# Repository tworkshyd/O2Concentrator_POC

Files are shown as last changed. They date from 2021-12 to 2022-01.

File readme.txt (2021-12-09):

#### Log of Firmware development ################

 5th May 2021 
	# development started

17th May 2021 
	# 1st test build released
         - O2 generation logic as per oxikit implemented

22th May 2021
	# 2nd test build released 
	 - ON/OFF switch incorporated

08 Sep 2021
	# 3rd test build working on first hand prototyped hardware
		with 3_2_valve_versions_900gms_08092021

13 Sep 2021
	# Board bringup for Rev 1.0 h/w started

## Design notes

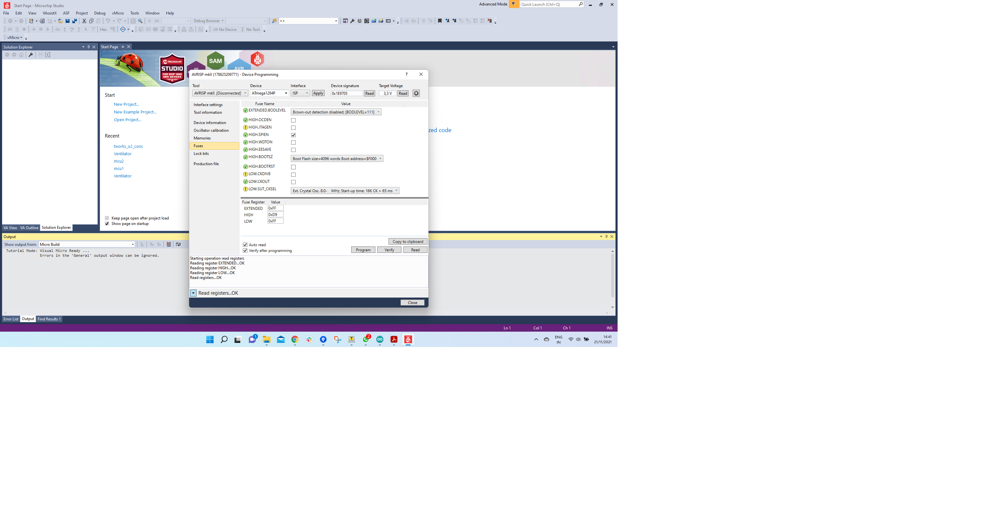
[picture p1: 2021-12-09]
tworks_o2_cons_docs/Fuse-bits-to-program.png

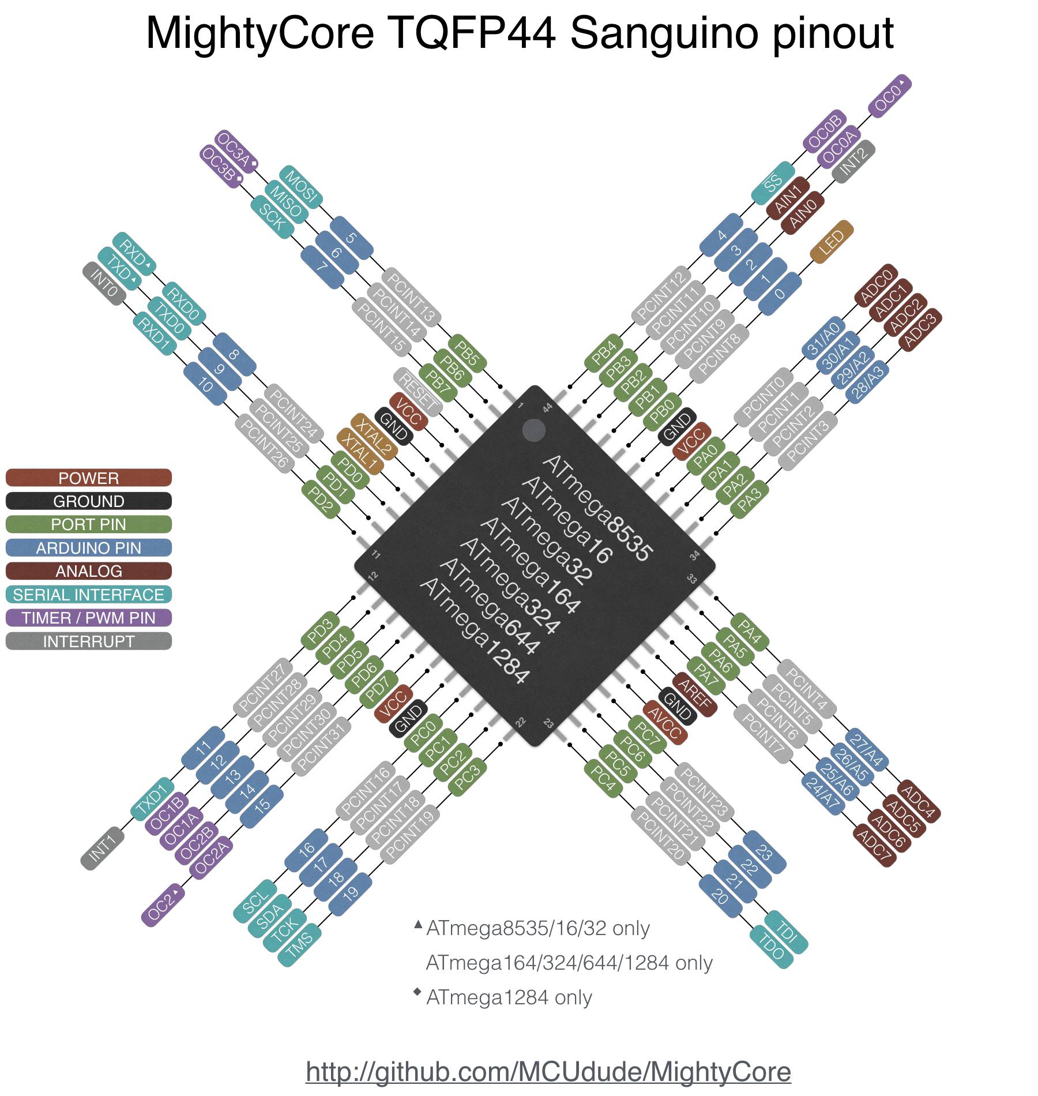
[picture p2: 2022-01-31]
tworks_o2_cons_docs/Atmega-1284p-pin-out.jpg

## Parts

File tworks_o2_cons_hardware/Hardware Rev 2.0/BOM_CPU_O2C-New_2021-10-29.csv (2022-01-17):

ID | Name | Designator | Footprint | Quantity | Manufacturer Part | Manufacturer | Supplier | Supplier Part | Price
1 | Battery Holder CR2032 | B1 | BATTERY_CR2032 | 1
2 | 22pF | C1,C2 | C1206 | 2
3 | 100nF | C3,C6,C7,C8,C9,C10,C11,C12,C13,C15,C17,C18,C19,DCU3,DCU4,DCU5,DCU8 | C1206 | 17
4 | 10u | C4,C5 | EIA3216 | 2 | ?
5 | 0.33uF | C14 | C1206 | 1
6 | 1uF | C16 | C1206 | 1
7 | 47uF-100V-SMD | C20 | CAPAE1300X1400N | 1
8 | 1nF-2KV-1206-AVX | C21,C22 | CAPC3317X180N | 2
9 | 10uF-50V-1206 | C23,C24 | CAPC3216X190N | 2
10 | 330uF-50V-SMD | C25,C26 | CAPAE1300X1400N | 2
11 | 0.47mfd | C27 | 1206 | 1 | ?
12 | 33mfd | C28 | CAP-D5.0XF2.0 | 1 | ?
13 | M7_C84184 | D1,D2,D3 | SMA_L4.3-W2.6-LS5.2-RD | 3 | M7 | DYELEC | LCSC | C84184 | 0.011
14 | SM712 | D4 | SOT-23_L2.9-W1.3-P1.90-LS2.4-BR | 1 | SM712 | Yenji | LCSC | C127543
15 | TFZVTR9.1B | D5 | SOD-323HE_L2.0-W1.4-LS2.5-RD | 1 | TFZVTR9.1B | ROHM Semicon | LCSC | C117743 | 0.162
16 | FL2D-13-471R3 | FL1 | FL2D13471R3 | 1
17 | BOXHDR 2.54_2x10 | J1 | HDR-M-2.54_2X10 | 1 |  |  | LCSC | C124359 | 0.136
18 | HDR-F-2.54_2x3 | J2 | HDR-F-2.54_2X3 | 1 |  |  | LCSC | C65114 | 0.025
19 | BOXHDR 2.54_2x6 | J3 | HDR-M-2.54_2X6 | 1 |  |  | LCSC | C124388 | 0.071
20 | Berg 2 Pin | JMP1,JMP2,JMP3 | HDR-F-2.54_1X2 | 3 |  |  | LCSC | C49661 | 0.03
21 | Berg 3 Pin | JMP4 | HDR-F-2.54_1X3 | 1 |  |  | LCSC | C146690 | 0.068
22 | Berg 2 Pin | JMP5,JP4 | HDR-M-2.54_1X2 | 2 |  |  | LCSC | C124375 | 0.017
23 | Relimate 3 Pin | JP1,JP2 | HDR-M-2.54_1X3 | 2 |  |  | LCSC | C180248 | 0.236
24 | Relimate 3 Pin | JP3 | HDR-F-2.54_1X3 | 1 |  |  | LCSC | C146690 | 0.068
25 | 10uH | L1 | L_AXIAL-0.4 | 1
26 | LED 1206 Yellow | LED1,LED2 | LED 1206 RED | 2
27 | LED 1206 White | LED3 | LED 1206 RED | 1
28 | LED 1206 RED | LED4,LED5,LED6,LED7,LED8,LED9,LED10 | LED 1206 RED | 7
29 | CONN-TH_2P-P5.00 | P1,P2,P3,P4,P6 | CONN-TH_2P-P5.00 | 5 |  |  | LCSC
30 | 2N7002LT1H | Q1,Q2,Q3,Q5 | SOT23-3 | 4
31 | FQB22P10TM | Q4 | TO-263-3_L10.2-W10.7-P5.08-LS16.2-BR | 1 | FQB22P10TM | ON Semicon | LCSC | C108357 | 2.4
32 | BC847A | Q5~ | SOT-23-3_L2.9-W1.3-P1.90-LS2.4-BR | 1 | BC847A | Shenzhen Jinyu Semicon | LCSC | C259985 | 0.009
33 | 100R | R1,R2,R5 | R1206 | 3
34 | 99.9R | R3,R4 | AXIAL-0.4 | 2 | ?
35 | 120R | R6 | R1206 | 1
36 | 180R | R7,R8 | AXIAL-0.4 | 2 | ?
37 | 301R | R9,R10 | AXIAL-0.4 | 2 | ?
38 | 330R | R11,R12,R13,R14,R15,R15~ | R1206 | 6
39 | 500R | R16,R17 | AXIAL-0.4 | 2 | ?
40 | 510R | R18,R19,R20,R21 | R1206 | 4
41 | 680R | R22,R23 | R1206 | 2
42 | 750R | R24 | R1206 | 1
43 | 1k | R25,R26 | AXIAL-0.4 | 2 | ?
44 | 1.2K | R27,R28,R29,R30 | R1206 | 4
45 | 3.3K | R31,R32,R33,R34,R35 | R1206 | 5
46 | 3.32K | R36 | R1206 | 1
47 | 4.7K | R37,R38 | R1206 | 2
48 | 4.99k | R39,R40,R41,R42 | AXIAL-0.4 | 4 | ?
49 | 5.1K | R43,R44 | R1206 | 2
50 | 10K | R45,R46,R48,R49,R50,R51,R52 | R1206 | 7
51 | 10k | R47 | R1206 | 1
52 | 100k | R53 | R1206 | 1
53 | 105K | R54,R55 | AXIAL-0.4 | 2 | ?
54 | 0R | R56 | R1206 | 1
55 | SRD-05VDC-SL-C | RLY1,RLY2,RLY3 | RELAY-TH_SRD-XXVDC-XL-C | 3 | SRD-05VDC-SL-C | SONGLE | LCSC | C35449 | 0.418
56 | BUZZERPTH | SG1 | BUZZER-12MM | 1
57 | TestPin | TP1,TP2,TP3,TP4,TP5 | TESTPIN | 5
58 | ATMEGA164PA-AU | U1 | TQFP-44_L10.0-W10.0-P0.80-LS12.0-BL | 1 | ATMEGA164PA-AU | Microchip Tech | LCSC | C220668 | 2.902
59 | MAX485ECSA+ | U2 | SOIC-8 | 1
60 | AT24C64D-SSHM-B | U3 | SOIC-8_L4.9-W3.9-P1.27-LS6.0-BL | 1 | AT24C64D-SSHM-B | MICROCHIP | LCSC | C116707 | 1.777
61 | DS1307ZN+ | U4 | SOP-8_L4.9-W3.9-P1.27-LS6.0-BL | 1 | DS1307ZN+ | MAXIM | LCSC | C26858 | 1.587
62 | NUF8402MNT4G | U5,U6,U7 | DFN-16_L4.0-W1.6-P0.50-BL-EP | 3 | NUF8402MNT4G | ON Semicon | LCSC | C233420 | 0.416
63 | ULN2803ADWR | U8 | SOIC-18_L11.6-W7.5-P1.27-LS10.3-BL | 1 | ULN2803ADWR | TI | LCSC | C9683 | 2.443
64 | MPX5100AP | U9 | MPX5100AP | 1 | MPX5100AP | NXP Semiconductors | Mouser | 841-MPX5100AP
65 | MPXV5100GP | U10 | MPXV5100GP | 1
66 | INA826AIDR | U11,U12 | SOIC-8_150MIL | 2 | INA826AIDR | TI | LCSC | C38433 | 3.949
67 | MCP6002-ESN | U13 | SOIC-8 | 1
68 | ADS1115QDGSRQ1 | U14 | MSOP10 | 1
69 | ICL7660AIBAZA-T | U15 | SOIC-8_150MIL | 1 | ICL7660AIBAZA-T | Intersil | LCSC | C7881 | 0.985
70 | URB2405S-10WR3 | U16 | PWRM-TH_URBXXXXS-6WR3 | 1 | URB2405S-10WR3 | MORNSUN Guangzhou S& T | LCSC | C970774 | 13.739
71 | LM3940IMP-3.3NOPB | U17 | SOT-223 | 1
72 | 16MHz | X1 | HC-49S_L11.0-W4.4-P4.88 | 1 | 49S DIP Crystal insulation film | YXC | LCSC | C35018 | 0.007
73 | 32.768KHz | X2 | 32K_CRYSTAL_BODYGND_FPRNT_MBR_2 | 1 | TDXLF-308 32.768KHZ 12.5PF 20PPM | TAE | LCSC | C145164 | 0.067
74 | XBEE-1B1 | XB1 | XBEE-1 | 1

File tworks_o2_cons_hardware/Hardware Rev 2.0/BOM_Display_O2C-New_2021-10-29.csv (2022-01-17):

ID | Name | Designator | Footprint | Quantity | Manufacturer Part | Manufacturer | Supplier | Supplier Part | Price
1 | 100nF | C1,C2,C3,DCNP1,DCNP2,DCNP3,DCNP4,DCU1,DCU2,DCU2-1,DCU2-2,DCU2-3 | C1206 | 12
2 | SUPERCAP 1F | C9 | SUPERCAPACITOR 1F | 1
3 | 1N4007R | D1 | DO-41_BD2.4-L4.7-P8.70-D0.9-RD | 1 | 1N4007R | Chongqing Pingwei Tech | LCSC | C432606 | 0.016
4 | 0.56" 7 segment display common cathode | DISP1,DISP2,DISP3,DISP4,DISP5 | LEDSEG_1_0.56_CATHODE | 5 | SC56-11SYKWA | Kingbright | RS-Online | 877-1555
5 | HDR-M-2.54_1x3 | J1,J2 | HDR-M-2.54_1X3 | 2 |  |  | LCSC | C180248 | 0.236
6 | HDR-M-2.54_2x10 | J3 | HDR-M-2.54_2X10 | 1 |  |  | LCSC | C124359 | 0.136
7 | HDR-M-2.54_1x4 | J4,J5 | HDR-M-2.54_1X4 | 2 |  |  | LCSC | C124378 | 0.028
8 | HDR-M-2.54_2x3 | JTAG1 | HDR-M-2.54_2X3 | 1 |  |  | LCSC | C65114 | 0.025
9 | 5050 SMD LED | LED1 | LED SMD 5050 | 1 | LEDSMD5050
10 | WS2812B-5050RGB | NPLED1,NPLED2,NPLED3,NPLED4 | LED-SMD_4P-L5.0-W5.0-BR_WS2812B-5050RGB | 4 | WS2812B-5050RGB | null | LCSC | C2838584
11 | BC558B | Q1 | TO-92-3_L4.9-W3.7-P1.27-L | 1 | BC558B | LGE | LCSC | C713619 | 0.019
12 | 330R | R1 | R1206 | 1
13 | 470R | R2,R3 | R1206 | 2
14 | 9.53K | R4 | R1206 | 1
15 | 10K | R5,R6,R7,R8,R9,R10,R11 | R1206 | 7
16 | 10k | R12,R13 | R1206 | 2
17 | BUZZERPTH | SG1 | BUZZER-12MM | 1
18 | MAX7219CWG+T | U1 | SOIC-24 | 1
19 | ATTINY85-20SU | U2 | SOIC-8_L5.3-W5.3-P1.27-LS8.0-BL | 1 | ATTINY85-20SU | MICROCHIP | LCSC | C89852 | 6.043
20 | XL74LS20 | U3 | SOP-14_L8.6-W3.9-P1.27-LS6.0-BL | 1 | XL74LS20 | XINLUDA | LCSC | C556253 | 0.151
21 | 100K | VR1 | RES-ADJ-TH_3296W | 1 | Pot-100R | ReliaPro | LCSC | C13649

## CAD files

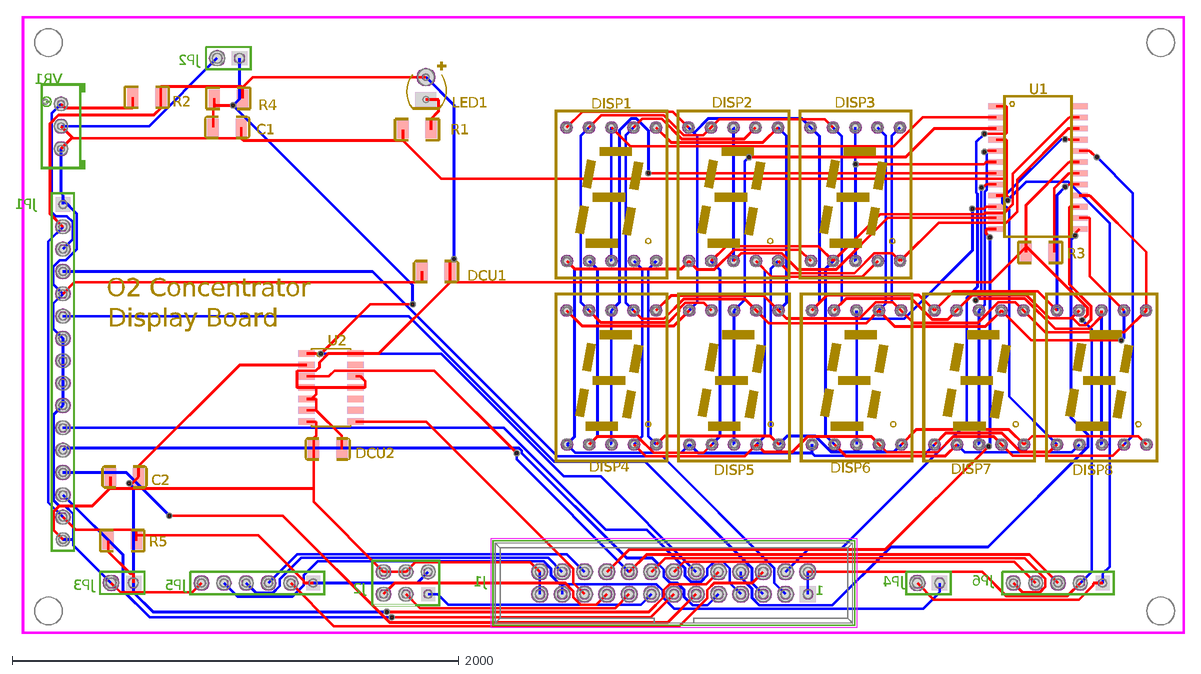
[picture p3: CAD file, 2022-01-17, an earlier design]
tworks_o2_cons_hardware/Hardware Rev 1.0/PCB_O2Conc-Display_2_2021-08-23.dxf
Display Board
O2 Concentrator
JP5
VR1
J1
1
JP6
JP1
J2
JP2
JP3
JP4
U1
LED1
DCU1
DCU2
DISP3
DISP2
DISP1
DISP5
DISP6
DISP8
DISP7
DISP4
R3
R2
R1
U2
C1
C2
R4
R5

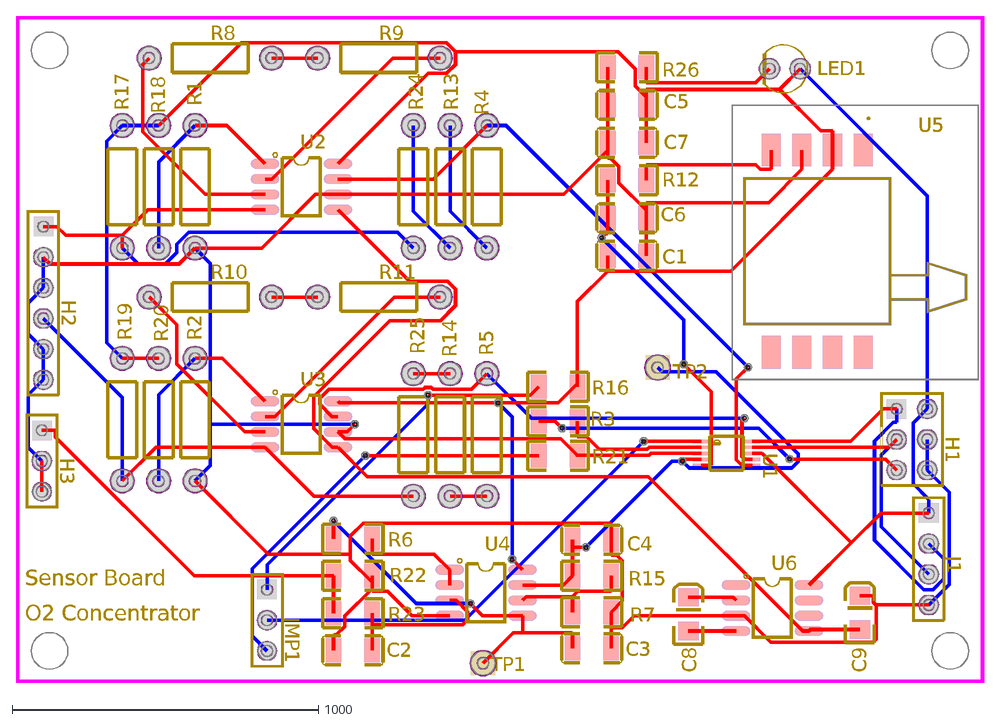
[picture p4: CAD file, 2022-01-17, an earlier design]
tworks_o2_cons_hardware/Hardware Rev 1.0/PCB_O2Conc_Sensorbrd_2021-08-23.dxf
O2 Concentrator
Sensor Board
J1
H2
R19
R20
R11
R5
R14
R25
R10
R2
R13
R9
R17
R18
R1
R8
R24
R4
U1
TP2
TP1
C3
C5
C6
C4
C2
C1
C7
JMP1
H3
U6
U5
U2
U3
C8
C9
H1
R23
R22
R12
R21
R16
R7
R15
R3
R6
U4
LED1
R26

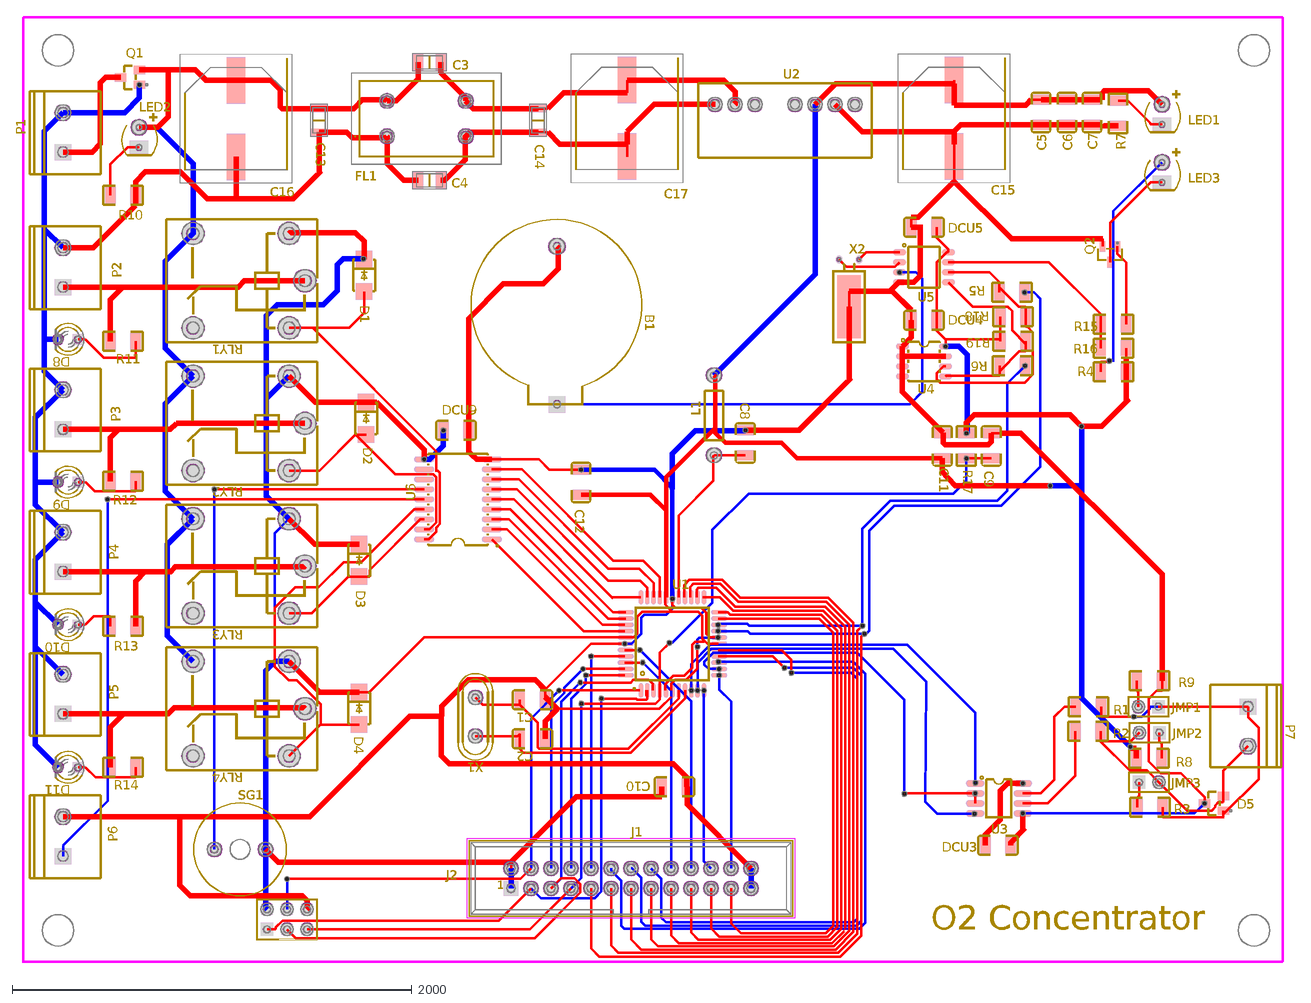
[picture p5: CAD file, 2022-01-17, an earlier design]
tworks_o2_cons_hardware/Hardware Rev 1.0/PCB_O2Concentrator_2021-08-23.dxf
O2 Concentrator
U6
D5
Q1
Q2
FL1
RLY2
RLY1
RLY3
RLY4
X2
B1
JMP3
JMP2
JMP1
D1
D3
D4
D2
P6
P5
P2
P3
P4
C17
C16
C15
U2
C4
C3
X1
LED3
LED2
LED1
J1
1
L1
C13
C14
D8
D9
D10
D11
C2
C1
DCU9
DCU3
C7
C12
C11
C10
C5
C9
C6
C8
U5
U3
J2
U4
R10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

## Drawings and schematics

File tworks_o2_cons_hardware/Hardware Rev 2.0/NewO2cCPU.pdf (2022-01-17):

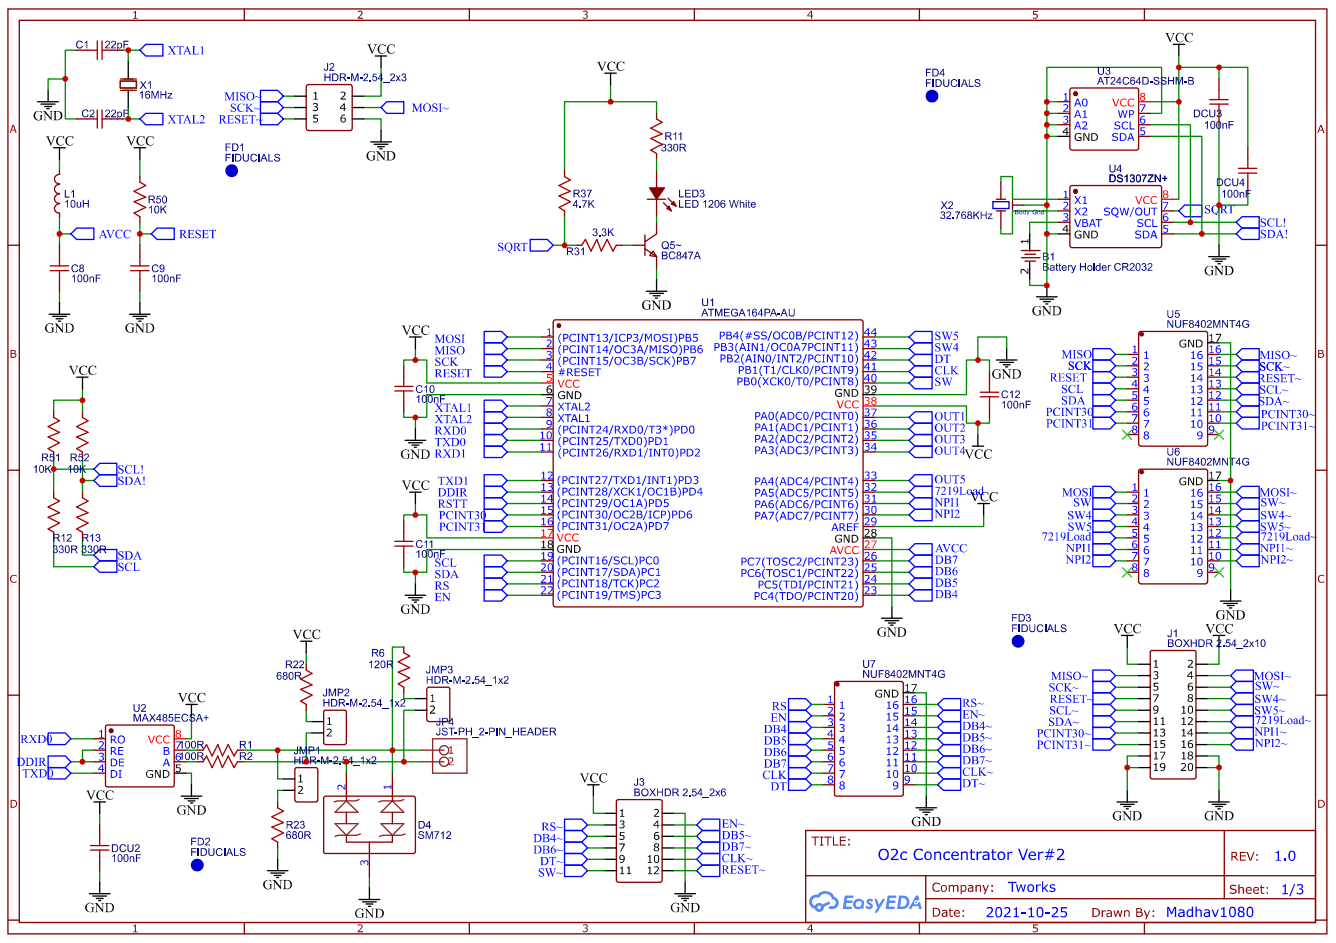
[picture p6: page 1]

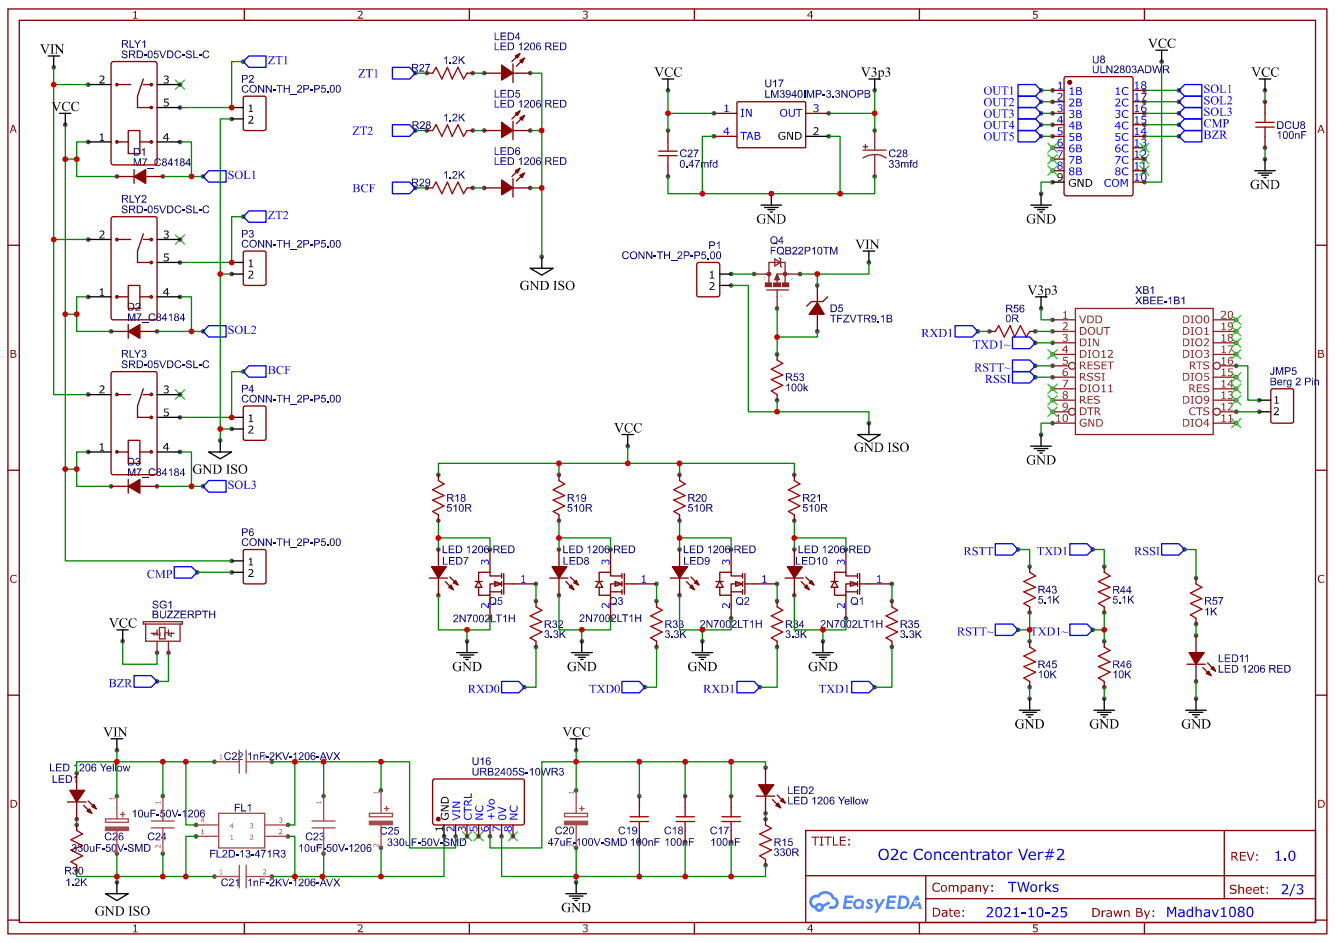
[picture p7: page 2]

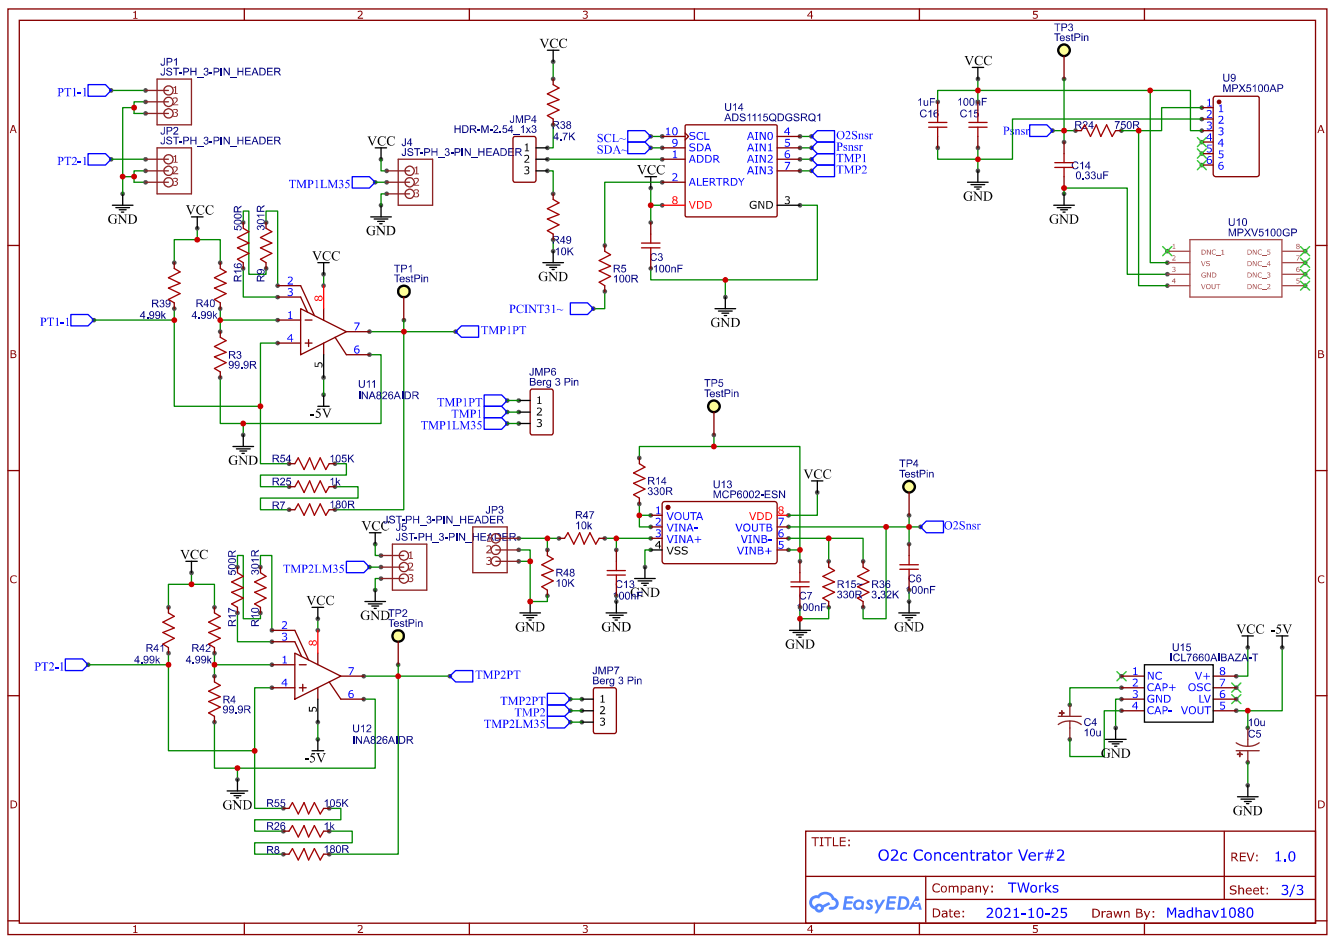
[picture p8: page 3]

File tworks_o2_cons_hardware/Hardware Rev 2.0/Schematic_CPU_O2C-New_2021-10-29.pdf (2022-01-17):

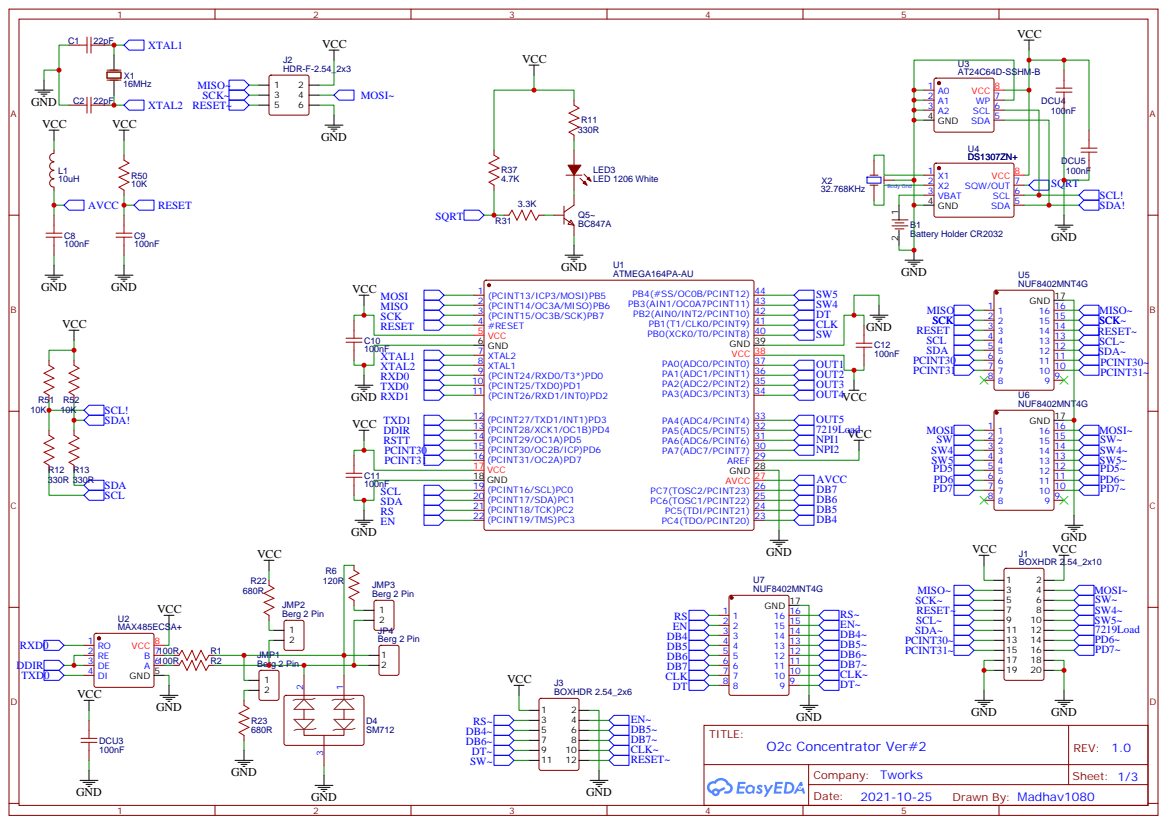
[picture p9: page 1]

# COM 10 8C 11 7C 12 6C 13 5C 14 4C 15 3C 16 2C 17 1C 18

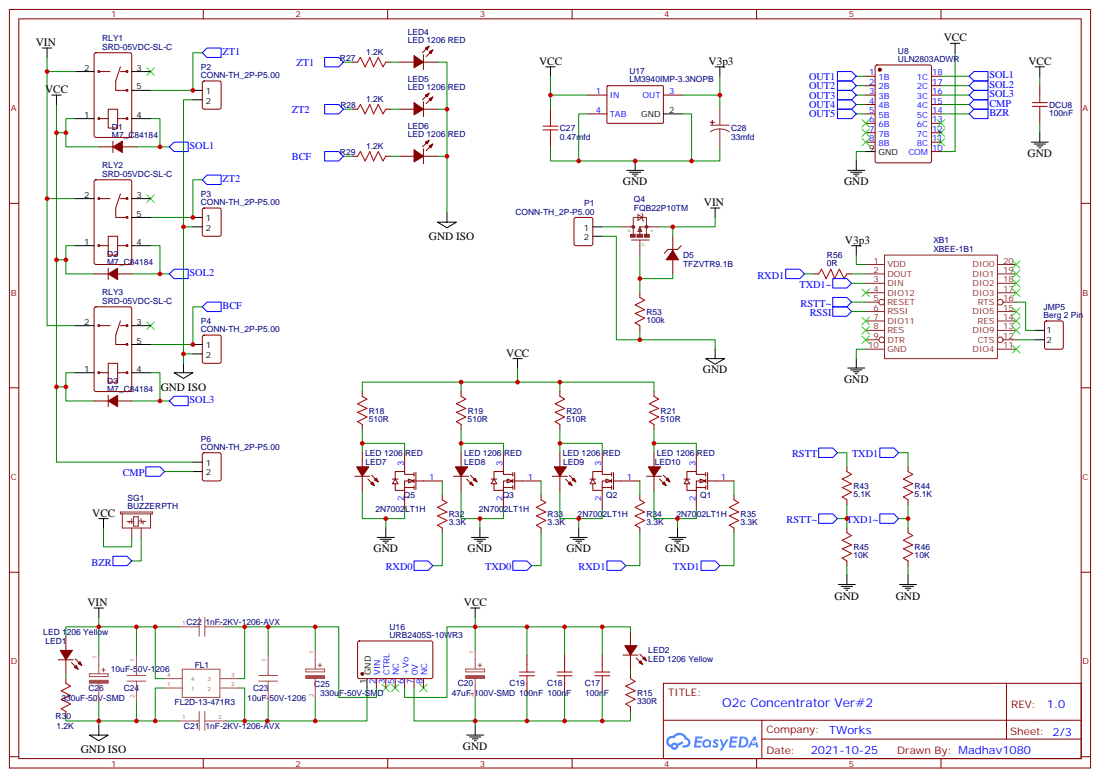
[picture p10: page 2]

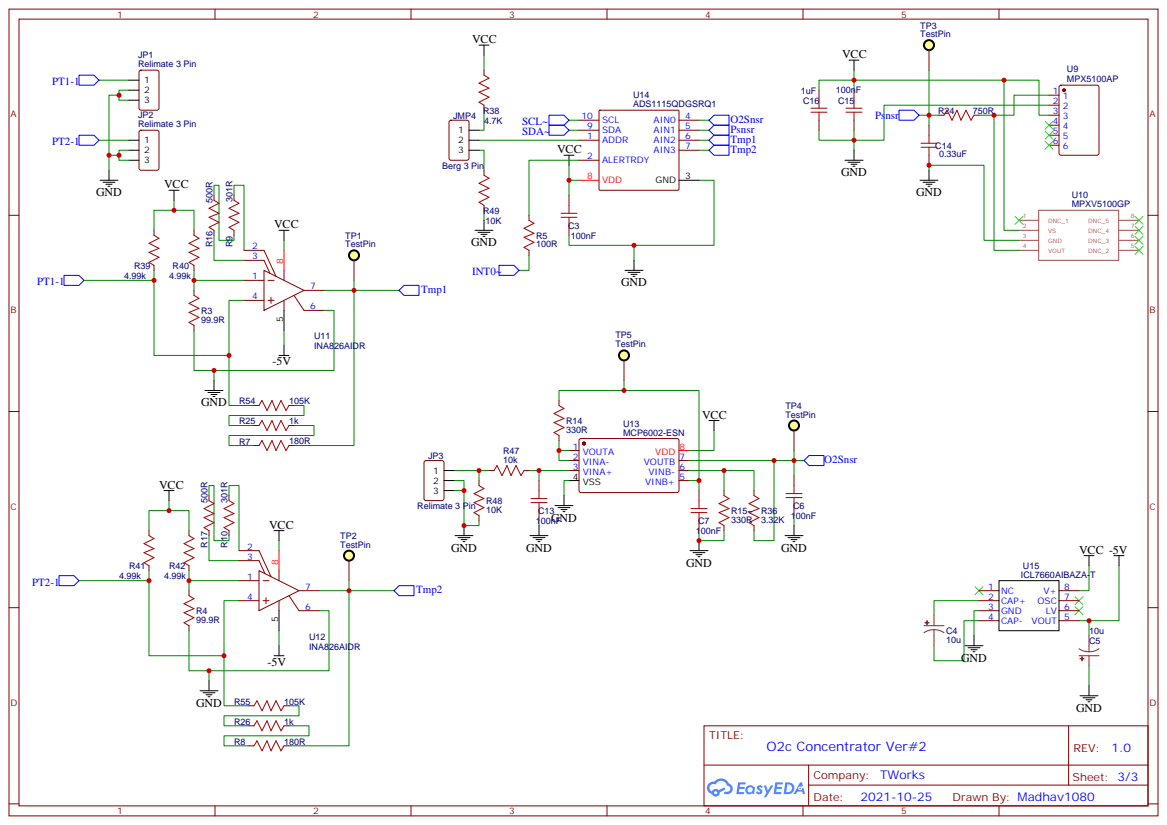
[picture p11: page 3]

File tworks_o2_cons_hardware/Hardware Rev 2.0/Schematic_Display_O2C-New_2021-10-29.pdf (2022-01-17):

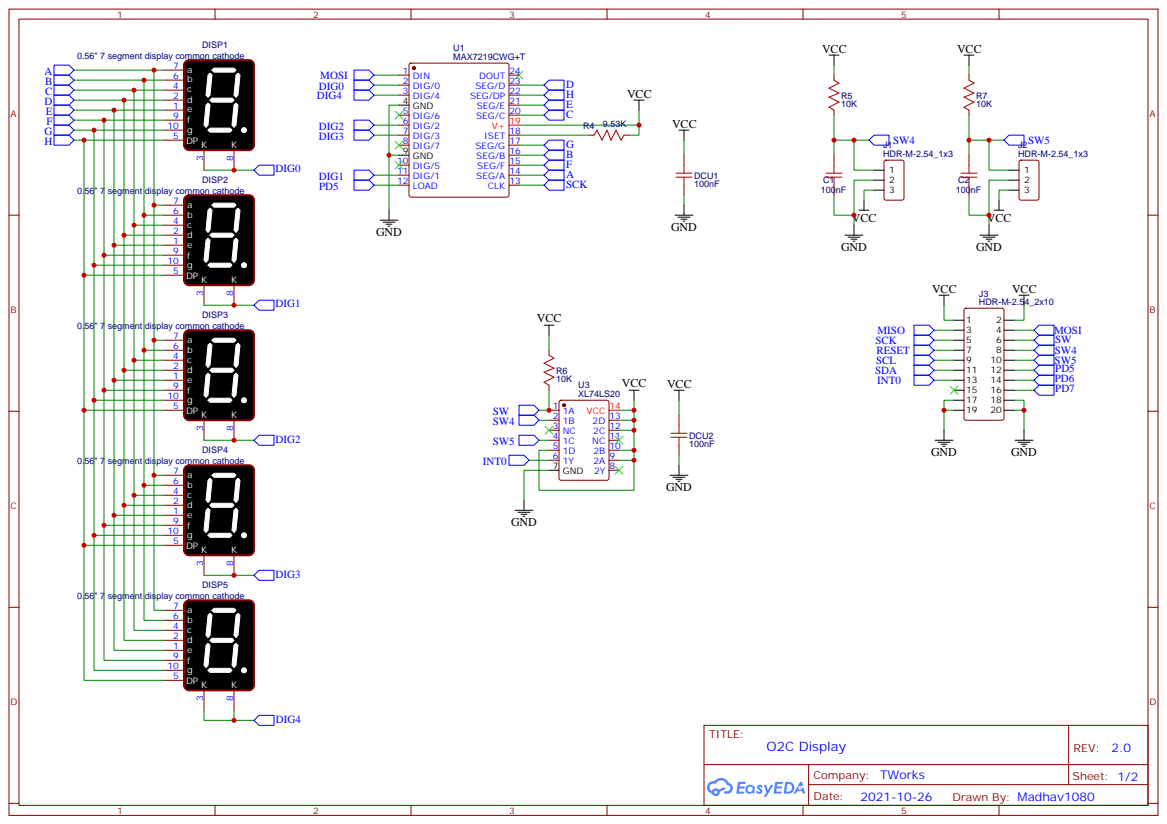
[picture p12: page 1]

0.56" 7 segment display common cathode

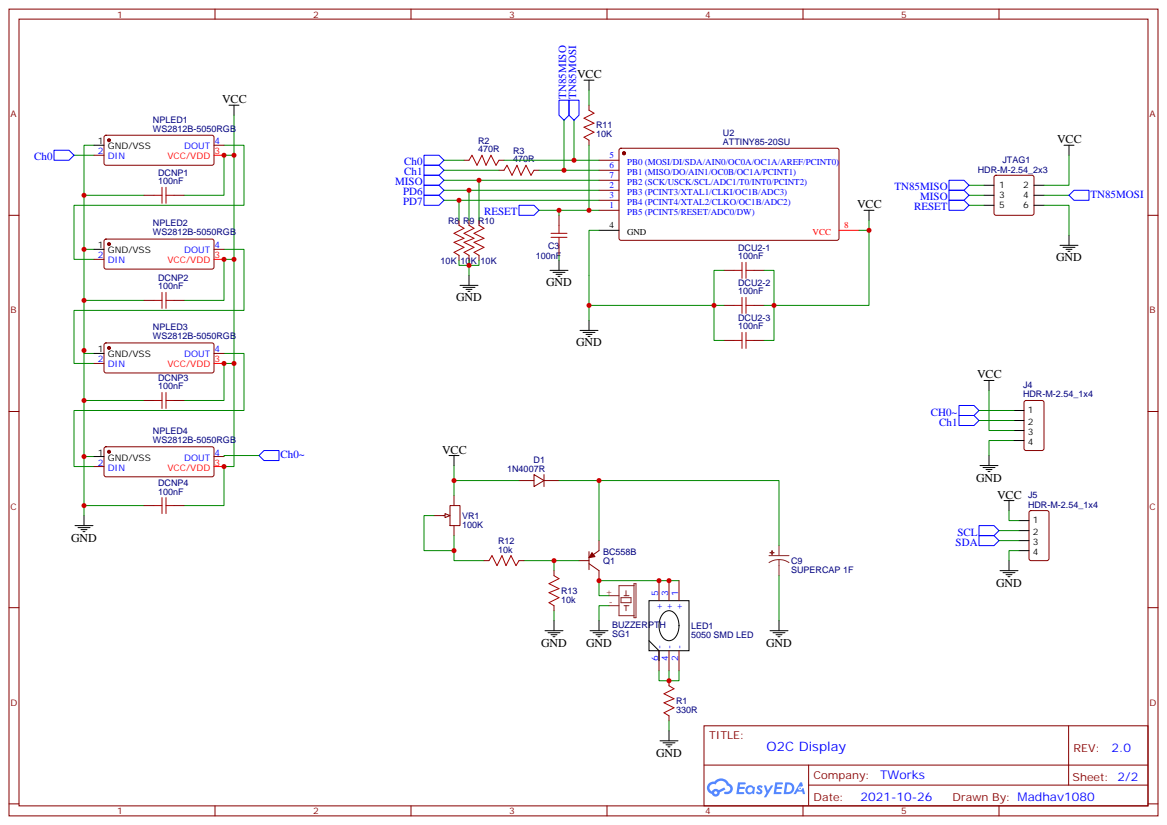
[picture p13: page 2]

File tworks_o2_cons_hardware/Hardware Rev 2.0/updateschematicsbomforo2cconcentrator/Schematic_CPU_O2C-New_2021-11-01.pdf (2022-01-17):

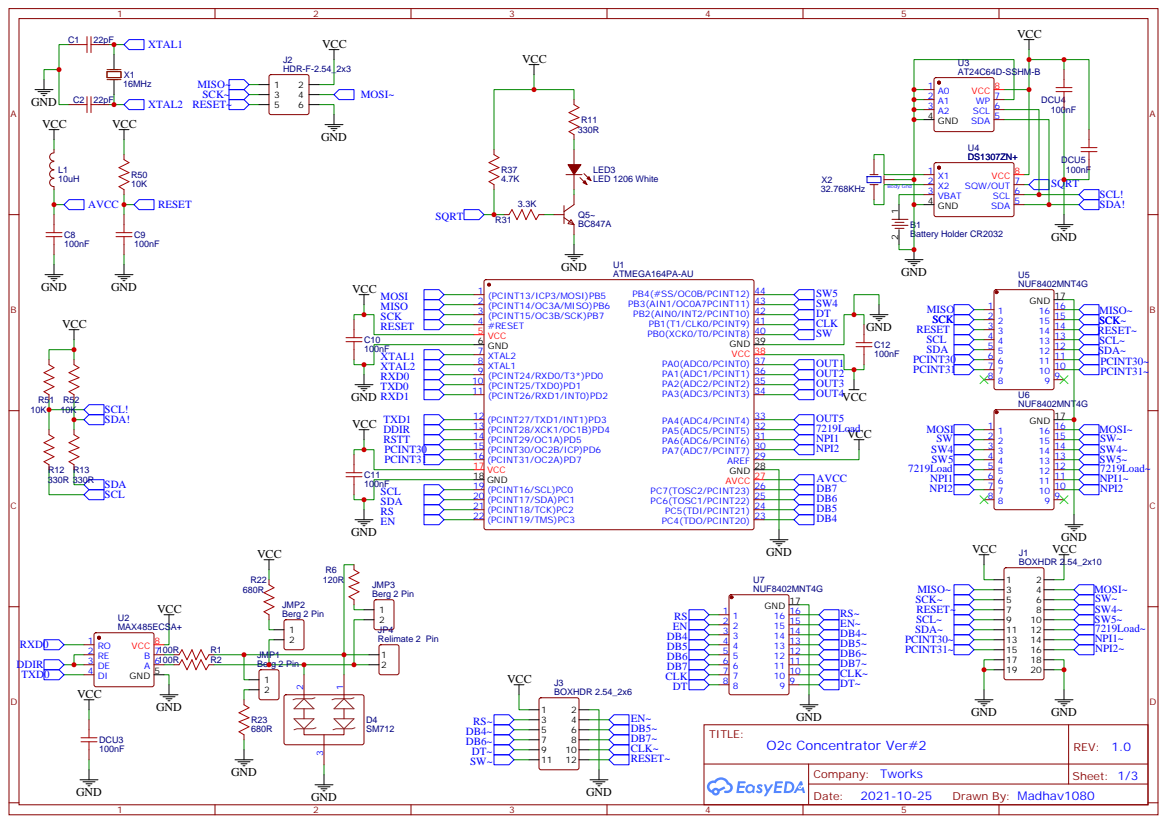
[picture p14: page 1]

# COM 10 8C 11 7C 12 6C 13 5C 14 4C 15 3C 16 2C 17 1C 18

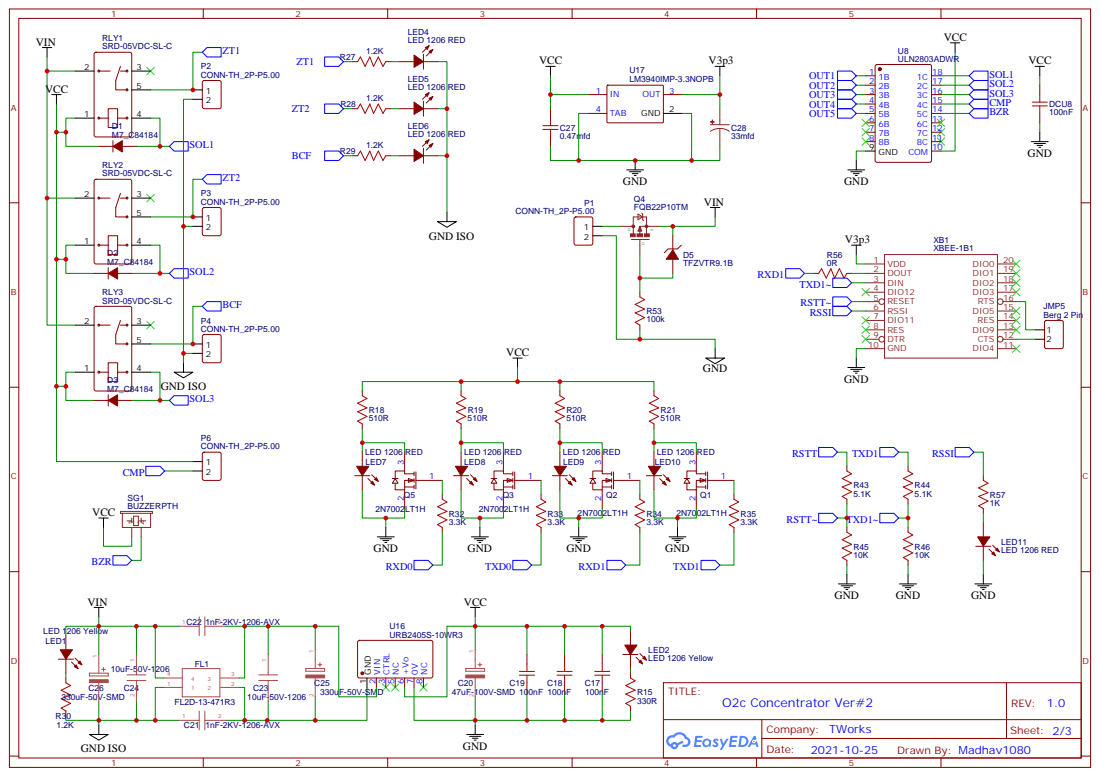
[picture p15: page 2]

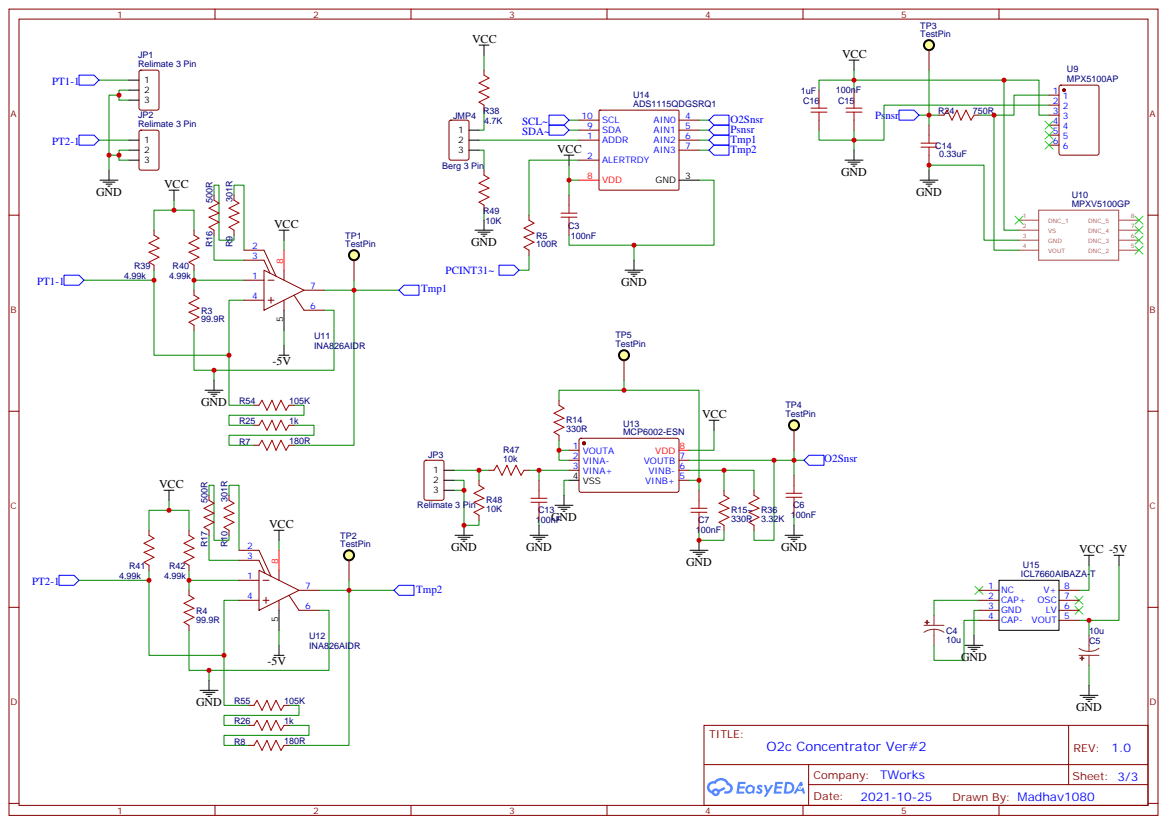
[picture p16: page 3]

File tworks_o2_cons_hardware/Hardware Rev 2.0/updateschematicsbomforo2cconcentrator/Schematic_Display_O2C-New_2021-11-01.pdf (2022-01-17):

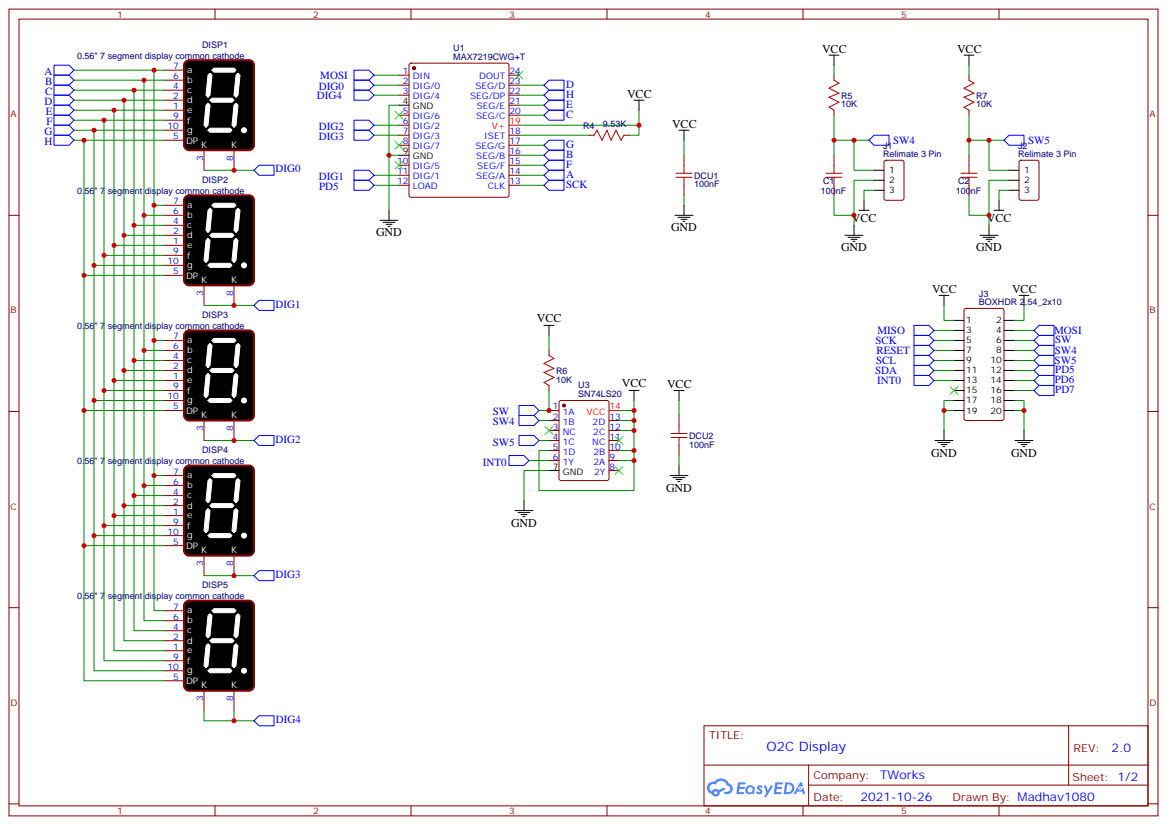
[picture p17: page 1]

0.56" 7 segment display common cathode





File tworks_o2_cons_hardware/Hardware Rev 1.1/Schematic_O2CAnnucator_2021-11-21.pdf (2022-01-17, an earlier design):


Drawn By: Rohan Rege

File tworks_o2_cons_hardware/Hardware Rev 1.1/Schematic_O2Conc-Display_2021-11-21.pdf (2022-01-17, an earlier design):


0.56" 7 segment display common cathode

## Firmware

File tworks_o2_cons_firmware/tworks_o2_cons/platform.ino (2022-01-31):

// platform.c


#include "platform.h"
#include "display.h"
#include "db.h"

// Note: timer 0 is not working with I2C peripheral, hence use Timer 1 / 2 for systick


void config_timer1  (void)  {

    // Timer 1
    TCCR1A = 0; // set entire TCCR0A register to 0
    TCCR1B = 0; // same for TCCR0B
    TCNT1  = 0; // initialize counter value to 0

    // set timer1 interrupt at 1kHz == 1msecs
    // set compare match register for 1khz increments
    OCR1A = 249; // = (16*10^6) / (1000*64) - 1 (must be < 66535)

    // set timer1 interrupt at 2kHz == 500usecs
    // set compare match register for 2khz increments
    // OCR1A = 124;  // = (16*10^6) / (2000*64) - 1 (must be < 66535)

    // turn on CTC mode
    TCCR1B |= (1 << WGM12);
    // Set CS12, CS11 and CS10 bits for 64 prescaler
    TCCR1B |= (1 << CS11) | (1 << CS10);

    // enable timer compare interrupt
    TIMSK1 |= (1 << OCIE1A);

}


void timer_init (void)  {

    cli();//stop interrupts
    config_timer1 ();
    sei();//allow interrupts

    DBG_PRINTLN ("Timer initialized..");
}

ISR (TIMER1_COMPA_vect) { // change the 0 to 1 for timer0

    // interrupt commands here
    systemtick_msecs++;

    f_msec = 1;
    if ( (systemtick_msecs % 10) == 0)  {
        f_10msec = 1;
        if ( (systemtick_msecs % 100) == 0)  {
            f_100msec = 1;
            if ( (systemtick_msecs % 1000) == 0)  {
                f_1sec = 1;
                systemtick_secs++;
                if (systemtick_secs >= 60)  {
                    systemtick_secs = 0;
                    f_1min = 1;
                    systemtick_mins++;
                    if (systemtick_mins >= 60) {
                        systemtick_mins = 0;
                        f_1hr = 1;
                        systemtick_hrs++;
                    }
                }
            }
        }
    }
}


void new_delay_msecs (unsigned int  time_delay) {

    unsigned long int   time_tag;


    time_tag = systemtick_msecs;
    while (time_elapsed (time_tag) < time_delay)
    {
        // nop
    }
}


void platform_init (void) {

    timer_init ();

    // set up the LCD's number of columns and rows:
    lcd.begin(LCD_COLS, LCD_ROWS);

    // pin mode setting
    pinMode(RLY_1,            OUTPUT);
    pinMode(RLY_2,            OUTPUT);
    pinMode(RLY_3,            OUTPUT);
#if   (HW_REVISION == HW_REV_1_0)
    pinMode(RLY_4,            OUTPUT);
#elif (HW_REVISION == HW_REV_2_0)
	// nop
#else
	// nop
#endif
	
    pinMode(DDIR,             OUTPUT);
    digitalWrite(DDIR,        HIGH);

    pinMode(buzzr_cntrl_pin,  OUTPUT);
    pinMode(compr_cntrl_pin,  OUTPUT);
    pinMode(startSwitchPin,   INPUT );
    pinMode(startSwitchPin,   INPUT_PULLUP);
    pinMode(alarmClearButton, INPUT );
    pinMode(alarmClearButton, INPUT_PULLUP);
    
    // default pin-state
    digitalWrite(buzzr_cntrl_pin,   LOW);
    digitalWrite(compr_cntrl_pin,   LOW );

    // Serial 7 segment interface
    pinMode(dataPin_7segment,       OUTPUT);
    pinMode(clckPin_7segment,       OUTPUT);
    pinMode(loadPin_7segment,       OUTPUT);

    digitalWrite(dataPin_7segment,  LOW );
    digitalWrite(clckPin_7segment,  LOW );
    digitalWrite(loadPin_7segment,  LOW );

    // neo-pixel leds interface
    pinMode(miso_neo_data1,         OUTPUT);
    pinMode(pd6_neo_data2,          OUTPUT);
    pinMode(pd7_neo_data3,          OUTPUT);

    digitalWrite(miso_neo_data1,    LOW );
    digitalWrite(pd6_neo_data2,     LOW );
    digitalWrite(pd7_neo_data3,     LOW );

    DBG_PRINTLN("GPIO init done..");

}


// void test_gpios (void) {
// 
// // 	timer_init ();
// 
// 	// set up the LCD's number of columns and rows:
// 	lcd.begin(LCD_COLS, LCD_ROWS);
// 
// 	DBG_PRINTLN("GPIO testing...");
// 
// 	// pin mode setting
// 	pinMode (RLY_1,            OUTPUT);
// 	DBG_PRINTLN ("RLY_1 = HIGH");
// 	digitalWrite (RLY_1,        HIGH);
// 	delay(1300);
// 	DBG_PRINTLN ("RLY_1 = low");
// 	digitalWrite (RLY_1,        LOW);
// 	delay(1300);
// 	
// 	pinMode (RLY_2,            OUTPUT);
// 	DBG_PRINTLN ("RLY_2 = HIGH");
// 	digitalWrite (RLY_2,        HIGH);
// 	delay(1300);
// 	DBG_PRINTLN ("RLY_2 = low");
// 	digitalWrite (RLY_2,        LOW);
// 	delay(1300);
// 
// 	pinMode (RLY_3,            OUTPUT);
// 	DBG_PRINTLN ("RLY_3 = HIGH");
// 	digitalWrite (RLY_3,        HIGH);
// 	delay(1300);
// 	DBG_PRINTLN ("RLY_3 = low");
// 	digitalWrite (RLY_3,        LOW);
// 	delay(1300);
// 
// 	#if   (HW_REVISION == HW_REV_1_0)
// 		pinMode (RLY_4,            OUTPUT);
// 		DBG_PRINTLN ("RLY_4 = HIGH");
// 		digitalWrite (RLY_4,        HIGH);
// 		delay(1300);
// 		DBG_PRINTLN ("RLY_4 = low");
// 		digitalWrite (RLY_4,        LOW);
// 		delay(1300);
// 	#elif (HW_REVISION == HW_REV_2_0)
// 		// nop
// 	#else
// 		// nop
// 	#endif
// 	
// 	pinMode (DDIR,            OUTPUT);
// 	DBG_PRINTLN ("DDIR = HIGH");
// 	digitalWrite (DDIR,        HIGH);
// 	delay(1300);
// 	DBG_PRINTLN ("DDIR = low");
// 	digitalWrite (DDIR,        LOW);
// 	delay(1300);
// 
// 	DBG_PRINTLN ("setting to default state.");
// 	DBG_PRINTLN ("DDIR = HIGH");
// 	digitalWrite(DDIR,        HIGH);
// 
// 	pinMode (buzzr_cntrl_pin,  OUTPUT);
// 	DBG_PRINTLN ("buzzr_cntrl_pin = HIGH");
// 	digitalWrite (buzzr_cntrl_pin,        HIGH);
// 	delay(1300);
// 	DBG_PRINTLN ("buzzr_cntrl_pin = low");
// 	digitalWrite (buzzr_cntrl_pin,        LOW);
// 	delay(1300);
// 
// 	pinMode(compr_cntrl_pin,             OUTPUT);
// 	DBG_PRINTLN ("compr_cntrl_pin = HIGH");
// 	digitalWrite (compr_cntrl_pin,        HIGH);
// 	delay(1300);
// 	DBG_PRINTLN ("compr_cntrl_pin = low");
// 	digitalWrite (compr_cntrl_pin,        LOW);
// 	delay(1300);
// 
// 	
// 	// default pin-state
// 	digitalWrite(buzzr_cntrl_pin,   LOW);
// 	DBG_PRINTLN ("buzzr_cntrl_pin = HIGH");
// 	digitalWrite (buzzr_cntrl_pin,        HIGH);
// 	delay(1300);
// 	DBG_PRINTLN ("buzzr_cntrl_pin = low");
// 	digitalWrite (buzzr_cntrl_pin,        LOW);
// 	delay(1300);
// 
// 
// 	// Serial 7 segment interface
// 	pinMode(dataPin_7segment,       OUTPUT);
// 	DBG_PRINTLN ("compr_cntrl_pin = HIGH");
// 	digitalWrite (compr_cntrl_pin,        HIGH);
// 	delay(1300);
// 	DBG_PRINTLN ("compr_cntrl_pin = low");
// 	digitalWrite (compr_cntrl_pin,        LOW);
// 	delay(1300);
// 
// 	pinMode(clckPin_7segment,       OUTPUT);
// 	DBG_PRINTLN ("compr_cntrl_pin = HIGH");
// 	digitalWrite (compr_cntrl_pin,        HIGH);
// 	delay(1300);
// 	DBG_PRINTLN ("compr_cntrl_pin = low");
// 	digitalWrite (compr_cntrl_pin,        LOW);
// 	delay(1300);
// 
// 	pinMode(loadPin_7segment,       OUTPUT);
// 	DBG_PRINTLN ("compr_cntrl_pin = HIGH");
// 	digitalWrite (compr_cntrl_pin,        HIGH);
// 	delay(1300);
// 	DBG_PRINTLN ("compr_cntrl_pin = low");
// 	digitalWrite (compr_cntrl_pin,        LOW);
// 	delay(1300);
// 
// 
// 	DBG_PRINTLN ("setting to default state...");
// 	digitalWrite(dataPin_7segment,  LOW );
// 	digitalWrite(clckPin_7segment,  LOW );
// 	digitalWrite(loadPin_7segment,  LOW );
// 
// 	// neo-pixel leds interface
// 	pinMode(miso_neo_data1,         OUTPUT);
// 	DBG_PRINTLN ("miso_neo_data1 = HIGH");
// 	digitalWrite (miso_neo_data1,        HIGH);
// 	delay(1300);
// 	DBG_PRINTLN ("miso_neo_data1 = low");
// 	digitalWrite (miso_neo_data1,        LOW);
// 	delay(1300);
// 
// 	pinMode(pd6_neo_data2,          OUTPUT);
// 	DBG_PRINTLN ("pd6_neo_data2 = HIGH");
// 	digitalWrite (pd6_neo_data2,        HIGH);
// 	delay(1300);
// 	DBG_PRINTLN ("pd6_neo_data2 = low");
// 	digitalWrite (pd6_neo_data2,        LOW);
// 	delay(1300);
// 
// 	pinMode(pd7_neo_data3,          OUTPUT);
// 	DBG_PRINTLN ("pd7_neo_data3 = HIGH");
// 	digitalWrite (pd7_neo_data3,       HIGH);
// 	delay(1300);
// 	DBG_PRINTLN ("pd7_neo_data3 = low");
// 	digitalWrite (pd7_neo_data3,        LOW);
// 	delay(1300);
// 
// 
// 	DBG_PRINTLN ("setting to default state..");
// 	digitalWrite(miso_neo_data1,    LOW );
// 	digitalWrite(pd6_neo_data2,     LOW );
// 	digitalWrite(pd7_neo_data3,     LOW );
// 
// 	DBG_PRINTLN("GPIO init done..");
// 
// }

bool do_control (DO_CONTROLS_E do_id, bool bit_value) {


    // DBG_PRINT ("do_id : ");
    // DBG_PRINTLN (do_id);

    switch (do_id)
    {
        case SIEVE_A_VALVE_CONTROL:
            digitalWrite(Sieve_A_Valve_Z1,      bit_value);
            break;
        case SIEVE_B_VALVE_CONTROL:
            digitalWrite(Sieve_B_Valve_Z2,      bit_value);
            break;
        case SIEVE_FLUSH_VLV_CNTRL:
            digitalWrite(PreCharge_Valve_BCKF,  bit_value);
            break;
        case COMPRESSOR_CONTROL:
            digitalWrite(compr_cntrl_pin,       bit_value);
            break;
        case BUZZER_CONTROL:
            digitalWrite(buzzr_cntrl_pin,       !bit_value);
            break;
        case _7SEG_DATA_CONTROL:
        case _7SEG_CLCK_CONTROL:
        case _7SEG_CS_CONTROL:
            break;
        default:
            do_id = INVALID_DO_ID;
            break;
    }


    if (do_id != INVALID_DO_ID)  {
        if (bit_value)  {
            do_byte |= do_id;
        }
        else {
            do_byte &= ~do_id;
        }
    }


}



unsigned long int time_elapsed (unsigned long int time_delay)  {

    return systemtick_msecs - time_delay;

}





/////////////////// scrap area /////////////////////////////////

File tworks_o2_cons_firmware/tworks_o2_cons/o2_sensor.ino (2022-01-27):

// o2_sensor.c


#include "platform.h"
#include "o2_sensor.h"
#include "ADS1X15.h"
#include "config.h"




volatile int16_t  o2_raw_adc_count;
volatile float    o2_m_raw_voltage;

// for single point calibration
volatile float    o2_calib_const;

// for two / multi point calibration
volatile float    o2_slope;
volatile float    o2_offset_value;

float y_samples[NUM_OF_SAMPLES_O2]     = {  1.0,    20.9,   99.0};			// based on o2c tank purity = 96% & nitrogen tank purity = 95%

// Hard coding calibration parameters for all 5 machines.
#if    (O2_SENSOR == 1)
	// 1. for Envitec sensor marked as S1 for demo device
	float x_samples[NUM_OF_SAMPLES_O2]     = { 7.55, 566.63, 570.0};		// default calib values

#elif  (O2_SENSOR == 2)
	// 2. for Envitec sensor marked as S2 for demo device
	float x_samples[NUM_OF_SAMPLES_O2]     = { 19.5, 130.5,  628.9};		// default calib values

#elif  (O2_SENSOR == 3)
	// 3. for Envitec sensor marked as S3 for demo device
	float x_samples[NUM_OF_SAMPLES_O2]     = { 21.25, 134.0,  637.63};		// default calib values

#elif  (O2_SENSOR == 4)
	// 1. for Envitec sensor marked as S1 for demo device
	float x_samples[NUM_OF_SAMPLES_O2]     = { 24.88, 159.13, 675.0};		// default calib values

#elif  (O2_SENSOR == 5)
	// 2. for Envitec sensor marked as S2 for demo device
	float x_samples[NUM_OF_SAMPLES_O2]     = {  10.13, 142.0,  655.25};     // default calib values

#elif  (O2_SENSOR == 6)
	// 2. for Envitec sensor marked as S2 for demo device
	float x_samples[NUM_OF_SAMPLES_O2]     = {  21.25, 130.38,  627.63};    // default calib values

#else
	float x_samples[NUM_OF_SAMPLES_O2]     = { 10.375, 129.25,  588.125};   // default calib values

#endif


//-------------------------------------------------------------------------------------------------------------
ADS1115 ADS(O2_SENSOR_ADS_ADDR);

void ads_init (void)  {

    DBG_PRINT("ADS1X15_LIB_VERSION: ");
    DBG_PRINTLN(ADS1X15_LIB_VERSION);

    // ads1015.setGain(GAIN_TWOTHIRDS); // 2/3x gain +/- 6.144V  1 bit = 3mV (default)
    // ads1015.setGain(GAIN_ONE);       // 1x gain   +/- 4.096V  1 bit = 2mV
    // ads1015.setGain(GAIN_TWO);       // 2x gain   +/- 2.048V  1 bit = 1mV
    // ads1015.setGain(GAIN_FOUR);      // 4x gain   +/- 1.024V  1 bit = 0.5mV
    // ads1015.setGain(GAIN_EIGHT);     // 8x gain   +/- 0.512V  1 bit = 0.25mV
    // ads1015.setGain(GAIN_SIXTEEN);   // 16x gain  +/- 0.256V  1 bit = 0.125mV

    ADS.begin();
    ADS.setGain(1);         // GAIN_ONE (for an input range of +/-4.096V)
    ADS.setDataRate(7);     // slow

    ADS.setMode(0);         // continuous mode
    ADS.readADC(O2_SENSOR_CHANNEL_NO);  

}

void test_ads1115 (void)  {
  
    ADS.setGain(0);
    
    while (1)
    {

        int16_t val_0 = ADS.readADC(0);  
        int16_t val_1 = ADS.readADC(1);  
        int16_t val_2 = ADS.readADC(2);  
        int16_t val_3 = ADS.readADC(3);  
        
        float f = ADS.toVoltage(1);  // voltage factor
        
        Serial.print("\tAnalog0: "); Serial.print(val_0); Serial.print('\t'); Serial.println(val_0 * f, 3);
        Serial.print("\tAnalog1: "); Serial.print(val_1); Serial.print('\t'); Serial.println(val_1 * f, 3);
        Serial.print("\tAnalog2: "); Serial.print(val_2); Serial.print('\t'); Serial.println(val_2 * f, 3);
        Serial.print("\tAnalog3: "); Serial.print(val_3); Serial.print('\t'); Serial.println(val_3 * f, 3);
        Serial.println();
        
        delay(1000);
    }
  
}



/*
    main function to calibrate and get m (slope) and c (constant) after curve fitting
    read y data from eeprom
    convert from byte to float
    use in algo to calc m and c values.
*/
void multi_point_calibration (void)  {

    float x = 0, y = 0;
    float sigmaX = 0, sigmaY = 0;
    float sigmaXX = 0, sigmaXY = 0;
    float denominator = 0;    
    int   value = 0;
    int   result;

    result = SUCCESS;

    for (int index = 0; index < NUM_OF_SAMPLES_O2; index++)
    {
        y = y_samples[index];
        x = x_samples[index];
        
        sigmaX  += x;
        sigmaY  += y;
        sigmaXX += x * x;
        sigmaXY += x * y;

//         DBG_PRINT ("      x : "); DBG_PRINTLN (x);        DBG_PRINT ("      y : "); DBG_PRINTLN (y);
//         DBG_PRINT (" sigmaX : "); DBG_PRINTLN (sigmaX);   DBG_PRINT (" sigmaY : "); DBG_PRINTLN (sigmaY);
//         DBG_PRINT ("sigmaXX : "); DBG_PRINTLN (sigmaXX);  DBG_PRINT ("sigmaXY : "); DBG_PRINTLN (sigmaXY);
    }
    
    denominator = (NUM_OF_SAMPLES_O2 * sigmaXX) - (sigmaX * sigmaX);
//     DBG_PRINT ("dnmnatr : "); DBG_PRINTLN (denominator);

    if (denominator != 0) {      
        o2_slope = ((NUM_OF_SAMPLES_O2 * sigmaXY) - (sigmaX * sigmaY)) / denominator;
        o2_offset_value = ((sigmaY * sigmaXX) - (sigmaX * sigmaXY)) / denominator;
        DBG_PRINTLN ("O2 calibration successful .!!");
        result = SUCCESS;
    } 
    else {      
        o2_slope = 0;
        o2_offset_value = 0;
        result =  ERROR_SENSOR_CALIBRATION;
        DBG_PRINTLN ("Error: O2 calibration failed!!");
    }

//     DBG_PRINTLN ("");
//     DBG_PRINT   ("o2_slope : ");
//     DBG_PRINT   (o2_slope);
//     DBG_PRINT   (", o2_offset_value : ");
//     DBG_PRINT   (o2_offset_value);

    
}


/*
    main function to calibrate and get m (slope) and c (constant) 
	using two points and slope formula.
*/
void two_point_calibration (void)  {

	// todo
	
}


/*
    Single point calibration.
*/
void single_point_calibration (void)  {


	// index '2' is for 99.5% oxygen calibration values
	o2_calib_const = y_samples[2] / x_samples[2];

    
}
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

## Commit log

2021-05-15 Pin mapping as per O2 proto circuit completed.
2021-05-18 Relay tests added on demand at power-up.
2021-05-19 Push button wiring changed by connecting it to GND instead of +Vcc, accordingly updated the code.
2021-05-22 Test release for testing, also to play around with valves ON/OFF timings to improve osigen concentration.
2021-05-24 I2C & ADS drivers integrated, able to read ADC output from O2 sensor.
2021-05-24 Sensor calibration menu .. under development.
2021-05-24 Valve operation logic reversed.
2021-05-24 Valve operation logic changed in test sequence code as well.
2021-05-24 Valves operation cross checked with sytem and updated the code.
2021-05-25 O2 sensor calibration values hard coded.. and being used..
2021-05-28 Pressure sensro MPX5100 code integrated.
2021-06-10 Routing valve controlling relays via 'do_control()' function.
2021-06-10 Adding selections for console prints viz. debug / periodic logs / event logs. etc.
2021-09-13 Working code tested on Prototyped hardware.
2021-09-13 Uploading Rev 1.0 hardware (with 4 PCB) boards, along with data sheets of major components used.
2021-09-18 Current run time and total run time values displayed on 7-segments.
2021-09-18 Initial valve positions set as per requirement.
2021-09-18 Fixed initial compressor ON before valves operation causing relif valve trigger.
2021-09-20 New pixcells LEDs configured for CRN and TRN indication.
2021-09-20 External EEPROM mempry map developed and displayed at powerup.
2021-09-21 LEDs added.
2021-09-22 Calibration values for Envitech O2 sensor S3 are hard coded for testing.
2021-09-23 Calibration constatns limits changed.
2021-09-23 Calibration constants again adjusted as per the purity of O2 and nitrogen cylinders.
2021-09-23 Calibration done for Envitec sensor S3, and corresponding readigns hard coded in 'o2_sensor.ino' file.. this a work around untill a proper user interface with a menu for calibration is developed.
2021-10-05 Display fine tuned .. to blank it with power-on, and start only when switch is pressed.
2021-11-05 Firmware version no. and PCB revision no.s are printed on debug console on power-on.
2021-11-05 Debug logs print buitified, and temperature sensor code files added.
2021-11-06 Temperature sensors reading working.. for both sensors.
2021-11-08 Neo-LEDs interfced, test code ran, working properly.
2021-11-10 CRN, TRN LEDs configured.
2021-11-10 This fixes CRN led blink (not staying continueously ON) bug.
2021-11-11 Alarm LEDs assigned.
2021-11-11 LED refresh logic optimized to skip off LEDs which are not ON in the same cycle.
2021-11-16 Neo-pixcell LEDs, first LED lighting up issue fixed.
2021-11-16 Neo-pixcel LED one more bugfixed and tested OK.
2021-11-23 In CRN display tried to print '-' in place of '.'
2021-11-24 Calibration values hard coded for O2 Sensor-001, Control Board -007, Sensor Board - 004
2021-11-24 Calibration values hard coded for O2 Sensor-002, Control Board -002, Sensor Board - 002
2021-11-24 Calibration values hard coded for O2 Sensor-003, Control Board -003, Sensor Board - 003
2021-11-24 Calibration values hard coded for O2 Sensor-004, Control Board -004, Sensor Board - 004
2021-11-24 Calibration values hard coded for O2 Sensor-005, Control Board -005, Sensor Board - 005
2021-11-25 Calibration values hard coded for O2 Sensor-006, Control Board -006, Sensor Board - 006
2021-12-06 Adding pressure sensor scan code.
2021-12-07 Pressure sensor ntegrated and calibrated for full scale from 0 - 23 psi.
2021-12-08 O2 sensor calibration values copied from GE tags.
2021-12-15 Temperature sensors T1 & T2 both are cheked for alarm generation with a condition if Temp > 150.0 *C it is treated as no sensor is connected (checked practically) and that particular sensor is ignore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
2021-12-23 7-segment display downsized in v2 to show only current run-hours.
2021-12-25 Neo-pixcel LEDs working and confgured them as per alarm sequence.
2022-01-14 All 4 values in cyclic order, O2, Press, Avg O2 and temprature. Current run time removed.
2022-01-17 Folders and their contents re-arranged.
    [BOM_CPU_O2C-New_2021-10-29.csv, BOM_CPU_O2C-New_2021-11-01.csv, BOM_Display_O2C-New_2021-10-29.csv, BOM_Display_O2C-New_2021-11-01.csv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]
2022-01-17 eePROM memory mapping done for run hours, calibration constantsts and periodic logs.
2022-01-17 logs printing done.. fine tuning tobe done.
2022-01-18 Serial prints edited and used sprintf() for standart formatted prints.
2022-01-18 O2 sensor calibration constants updated for 6 sensors.
2022-01-19 OneO2 sensor calibration constants updated for sensor #2.
2022-01-27 Single point calibration added .. by still keeping the multi point calibration .. one of them can be choosen using compiler directives.
2022-01-27 RoBOT external board interfaced with aurdino UNO board which intern interfaced with O2C board via-RS485 communication link.
2022-01-31 Atmega 1284p MCU pin-out and numbering image added to docs folder.
